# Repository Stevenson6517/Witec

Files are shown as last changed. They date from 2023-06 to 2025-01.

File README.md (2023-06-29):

# :microscope: WITec

A set of tools for interacting with and processing results from a WITec
AlphaSNOM.

> This project is currently in active development. Expect frequent
> breaking changes.

## Introduction

The tools and analysis provided by this repository attempt to recreate
some of the functionality of `ScanCtrlSpectroscopyPlus.exe` and
`WitecProject.exe` that are made available to the native Windows
installation associated with a WITec AlphaSNOM.

This repository aims to replace the proprietary `.WIP` (WitecProject
file) with an open-source [HDF5][hdf5] format that better withstands
data governance needs as they relate to external validation and
reproducibility that outlives the legacy software needed to operate this
equipment.

See a brief primer on [WITec formats](docs/witec_formats.md) for help in
understanding the data formats saved by _ScanCtrlSpectroscopyPlus_. The
analysis scripts work best on `.SPE` and `.WIP` files that have been
converted to `.hdf5` files.

[hdf5]: https://github.com/HDFGroup/hdf5

## Getting started

After cloning this repository, create a `witec` virtual environment from the
[environment.yaml](environment.yaml) file provided by this repository. Issue
the following command from a terminal navigated to the root of this project.

```python
conda env create -f environment.yaml
```

> Expect this process to take several minutes

Activate the environment before running any scripts:

```python
conda activate witec
```

See the [How To Guide](docs/how_to.md) for instructions on how to use
the instruments connected to the WITec AlphaSNOM in Stevenson 6517.

### Viewing Jupyter notebooks

Jupyter notebooks are a useful way to explore data and develop code
interactively, but they don't track well under version control. The
[jupytext][jupytext] extension for Jupyter Lab allows markdown files
(`.md`) and plain python files (`.py`) to be treated as interactive
python notebooks (`.ipynb`) while maintaining their simpler file formats
for better version control.

This project contains several Jupyter notebooks to help users understand
the scripts and types of data generated by the WITec AlphaSNOM. When you
first clone this repository, all notebooks will be in `.py` format, but
you can pair them to an interactive notebook or open them as an
interactive notebook with Jupytext. See their documentation on [paired
notebooks][jupytext-paired-notebooks] for help.

[jupytext]: https://jupytext.readthedocs.io/en/latest/
[jupytext-paired-notebooks]: https://jupytext.readthedocs.io/en/latest/paired-notebooks.html

## Contributing

Notice any errors? Tell us about them.

This lab is run by scientists, not software developers. Newcomers are welcome.
Check out our [guidelines](CONTRIBUTING.md) on how you can help.

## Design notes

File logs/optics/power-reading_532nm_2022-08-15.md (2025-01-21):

---
date: 2022-08-15
description: 'Laser power readings throughout the beampath'
measured by:
- David Curie
laser:
    - model: 'Verdi-5W'
    - serial: 'V5-G5403'
    - manufacture date: 'Dec-2004'
wavelength: 532
measurement:
    - device: 'Thorlabs PM101'
    - model: 'M00702598'
    - serial: '210608107'
    - calibration date: '2021-05-19'
    - mode: 'Mean over 4000 samples'
---

The measurements from Aug 14 suggest there is more loss than expected at each
of the microscope objectives. This suggests a misalignment of the fiber into
the microscope.

I adjusted the set screw on the SMA connector that brings the fiber into the
back of the WITec microscope until the laser spot size was minimized on the
camera. I then remeasured the power after each microscope objective.

| Location                        | Measured Power (mW) |
|---------------------------------|---------------------|
| After fiber exit                | 6.1  ± 0.3          |
| After 50x microscope objective  | 2.46 ± 0.12         |
| After 100x microscope objective | 0.84 ± 0.06         |

# Notes

- The laser from the fiber is directed down to the sample by use of a 50:50
  cube beam splitter. The theoretical maximum power that should reach the
  sample is 3 mW.
- The 100x objective has less throughput because it has a different numerical aperture (NA) than the 50x objective.
    - I have not quantified the beam size after the fiber or the theoretical throughput based on the NA. So long as I can quantify the power through the objective, I am not yet worried about optimizing the NA.

I next want to quantify the power at the sample based on various laser powers
as set by the power supply and by use of neutral density (ND) filters placed
before the objective coupling to the input of the fiber.

| Set Power (W) | ND Filter | Microscope Objective | Measured Power (µW) |
|---------------|-----------|----------------------|---------------------|
| 0.01          | ND10A     | 50x                  | 2.5  ± 0.1          |
| 0.10          | ND10A     | 50x                  | 42   ± 3            |
| 0.20          | ND10A     | 50x                  | 175  ± 8            |
| 0.30          | ND10A     | 50x                  | 380  ± 20           |
| 0.40          | ND10A     | 50x                  | 750  ± 30           |
| 0.50          | ND10A     | 50x                  | 1100 ± 50           |
| 0.60          | ND10A     | 50x                  | 1470 ± 70           |
| 0.70          | ND10A     | 50x                  | 1630 ± 70           |
| 0.80          | ND10A     | 50x                  | 1560 ± 60           |
| 0.90          | ND10A     | 50x                  | 1310 ± 60           |
| 1.00          | ND10A     | 50x                  | 960  ± 40           |
| 0.01          | ND20A     | 50x                  | 0.08 ± 0.01         |
| 0.10          | ND20A     | 50x                  | 2.0  ± 0.1          |
| 0.20          | ND20A     | 50x                  | 7.4  ± 0.4          |
| 0.30          | ND20A     | 50x                  | 18   ± 1            |
| 0.40          | ND20A     | 50x                  | 38   ± 2            |
| 0.50          | ND20A     | 50x                  | 65   ± 3            |
| 0.60          | ND20A     | 50x                  | 108  ± 5            |
| 0.70          | ND20A     | 50x                  | 155  ± 5            |
| 0.80          | ND20A     | 50x                  | 190  ± 10           |
| 0.90          | ND20A     | 50x                  | 230  ± 10           |
| 1.00          | ND20A     | 50x                  | 240  ± 10           |
| 0.01          | ND10A     | 100x                 | 0.17 ± 0.2          |
| 0.10          | ND10A     | 100x                 | 4.2  ± 0.3          |
| 0.20          | ND10A     | 100x                 | 16   ± 2            |
| 0.30          | ND10A     | 100x                 | 37   ± 2            |
| 0.40          | ND10A     | 100x                 | 69   ± 3            |
| 0.50          | ND10A     | 100x                 | 107  ± 5            |
| 0.60          | ND10A     | 100x                 | 153  ± 6            |
| 0.70          | ND10A     | 100x                 | 187  ± 7            |
| 0.80          | ND10A     | 100x                 | 215  ± 10           |
| 0.90          | ND10A     | 100x                 | 230  ± 10           |
| 1.00          | ND10A     | 100x                 | 210  ± 10           |
| 0.01          | ND20A     | 100x                 | 0.03 ± 0.01         |
| 0.10          | ND20A     | 100x                 | 0.68 ± 0.04         |
| 0.20          | ND20A     | 100x                 | 2.6  ± 0.2          |
| 0.30          | ND20A     | 100x                 | 6.4  ± 0.3          |
| 0.40          | ND20A     | 100x                 | 13.1 ± 0.6          |
| 0.50          | ND20A     | 100x                 | 23   ± 1            |
| 0.60          | ND20A     | 100x                 | 37   ± 2            |
| 0.70          | ND20A     | 100x                 | 52   ± 2            |
| 0.80          | ND20A     | 100x                 | 68   ± 4            |
| 0.90          | ND20A     | 100x                 | 80   ± 4            |
| 1.00          | ND20A     | 100x                 | 80   ± 4            |

```python
import pathlib

import matplotlib.pyplot as plt
import pandas as pd
import scienceplots

from markdown_tools import extract_data

# Gather variables from filename
filename = "power-reading_532nm_2022-08-15.md"
source = pathlib.Path(filename)
target = pathlib.Path("media") / source.name

verdi_power = extract_data(source, index=1)
# set boolean masks
ND10A = verdi_power["ND Filter"].isin(["ND10A"])
ND20A = verdi_power["ND Filter"].isin(["ND20A"])
obj_50 = verdi_power["Microscope Objective"].isin(["50x"])
obj_100 = verdi_power["Microscope Objective"].isin(["100x"])
# Use boolean masks to pick subsets of entire dataframe
ND10A_50 = verdi_power.loc[ND10A & obj_50]
ND10A_100 = verdi_power.loc[ND10A & obj_100]
ND20A_50 = verdi_power.loc[ND20A & obj_50]
ND20A_100 = verdi_power.loc[ND20A & obj_100]
# Plot each subset
with plt.style.context(["default", "science", "notebook"]):
    fig, [ax1, ax2] = plt.subplots(2, 1, figsize=(6, 8))
    fig.suptitle(source.stem)
    ND10A_50.plot(
        ax=ax1,
        y="Measured Power (µW)",
        yerr="± Measured Power (µW)",
        label="ND10A @ 50x",
    )
    ND20A_50.plot(
        ax=ax1,
        y="Measured Power (µW)",
        yerr="± Measured Power (µW)",
        label="ND20A @ 50x",
    )
    ND10A_100.plot(
        ax=ax1,
        y="Measured Power (µW)",
        yerr="± Measured Power (µW)",
        label="ND10A @ 100x",
    )
    ND20A_100.plot(
        ax=ax1,
        y="Measured Power (µW)",
        yerr="± Measured Power (µW)",
        label="ND20A @ 100x",
    )

    # Also plot weaker laser plots in separate plot for more detail
    ax2._get_lines.get_next_color()  # Skip 1st color so ax1 and ax2 match
    ND20A_50.plot(
        ax=ax2,
        y="Measured Power (µW)",
        yerr="± Measured Power (µW)",
        label="ND20A @ 50x",
    )
    ND10A_100.plot(
        ax=ax2,
        y="Measured Power (µW)",
        yerr="± Measured Power (µW)",
        label="ND10A @ 100x",
    )
    ND20A_100.plot(
        ax=ax2,
        y="Measured Power (µW)",
        yerr="± Measured Power (µW)",
        label="ND20A @ 100x",
    )
    ax1.set_ylabel("Measured Power (µW)")

    figname = target.with_suffix(".svg")
    fig.savefig(figname)
    print(f"Figure saved to {figname}")
plt.show()
```

power plots of laser at various filters and objectives Laser plots

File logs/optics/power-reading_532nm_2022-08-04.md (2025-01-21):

---
date: 2022-08-04
description: 'Laser power measurements in 6517 at the sample'
measured by:
- David Curie
- Alex Klapowitz
laser:
    - model: 'Verdi-5W'
    - serial: 'V5-G5403'
    - manufacture date: 'Dec-2004'
    - wavelength: 532
measurement:
    - device: 'Thorlabs PM101'
    - model: 'M00702598'
    - serial: '210608107'
    - calibration date: '2021-05-19'
    - mode: 'Mean over 4000 samples'
---

| Set Power (W) | ND Filter | Microscope Objective | Measured Power (µW) |
|---------------|-----------|----------------------|---------------------|
| 0.01          | None      | 50x                  | 1.62                |
| 0.02          | None      | 50x                  | 2.74                |
| 0.03          | None      | 50x                  | 3.85                |
| 0.04          | None      | 50x                  | 5.00 ± 0.14         |
| 0.05          | None      | 50x                  | 6.10 ± 0.16         |
| 0.06          | None      | 50x                  | 7.15 ± 0.2          |
| 0.07          | None      | 50x                  | 8.5  ± 0.2          |
| 0.08          | None      | 50x                  | 9.6  ± 0.2          |
| 0.09          | None      | 50x                  | 10.6 ± 0.3          |
| 0.10          | None      | 50x                  | 11.6 ± 0.3          |
| 0.11          | None      | 50x                  | 12.7 ± 0.3          |
| 0.12          | None      | 50x                  | 13.7 ± 0.3          |
| 0.13          | None      | 50x                  | 14.9 ± 0.4          |
| 0.14          | None      | 50x                  | 15.9 ± 0.5          |
| 0.15          | None      | 50x                  | 17.0 ± 0.5          |
| 0.16          | None      | 50x                  | 18.4 ± 0.4          |
| 0.17          | None      | 50x                  | 18.9 ± 0.5          |
| 0.18          | None      | 50x                  | 20.0 ± 0.5          |
| 0.19          | None      | 50x                  | 20.6 ± 0.5          |
| 0.20          | None      | 50x                  | 21.5 ± 0.6          |
| 0.25          | None      | 50x                  | 25.4 ± 0.7          |
| 0.30          | None      | 50x                  | 29.0 ± 0.7          |
| 0.35          | None      | 50x                  | 33.3 ± 0.9          |
| 0.40          | None      | 50x                  | 36.3 ± 1.0          |
| 0.45          | None      | 50x                  | 39.0 ± 1.1          |
| 0.50          | None      | 50x                  | 40.5 ± 1.1          |
| 0.55          | None      | 50x                  | 42.8 ± 0.8          |
| 0.60          | None      | 50x                  | 43.1 ± 1.1          |
| 0.01          | None      | 100x                 | 0.44 ± 0.02         |
| 0.02          | None      | 100x                 | 0.75 ± 0.02         |
| 0.03          | None      | 100x                 | 1.05 ± 0.03         |
| 0.04          | None      | 100x                 | 1.35 ± 0.04         |
| 0.05          | None      | 100x                 | 1.64 ± 0.04         |
| 0.06          | None      | 100x                 | 1.92 ± 0.05         |
| 0.07          | None      | 100x                 | 2.24 ± 0.03         |
| 0.08          | None      | 100x                 | 2.60 ± 0.06         |
| 0.09          | None      | 100x                 | 2.89 ± 0.08         |
| 0.10          | None      | 100x                 | 3.13 ± 0.08         |
| 0.11          | None      | 100x                 | 3.37 ± 0.10         |
| 0.12          | None      | 100x                 | 3.7  ± 0.1          |
| 0.13          | None      | 100x                 | 3.97 ± 0.08         |
| 0.14          | None      | 100x                 | 4.2  ± 0.1          |
| 0.15          | None      | 100x                 | 4.38 ± 0.12         |
| 0.16          | None      | 100x                 | 4.6  ± 0.1          |
| 0.17          | None      | 100x                 | 4.75 ± 0.11         |
| 0.18          | None      | 100x                 | 4.95 ± 0.15         |
| 0.19          | None      | 100x                 | 5.13 ± 0.13         |
| 0.20          | None      | 100x                 | 5.40 ± 0.14         |
| 0.25          | None      | 100x                 | 6.6  ± 0.2          |
| 0.30          | None      | 100x                 | 7.6  ± 0.2          |
| 0.35          | None      | 100x                 | 8.8  ± 0.3          |
| 0.40          | None      | 100x                 | 10.0 ± 0.3          |
| 0.45          | None      | 100x                 | 11.3 ± 0.3          |
| 0.50          | None      | 100x                 | 12.8 ± 0.4          |
| 0.55          | None      | 100x                 | 14.6 ± 0.4          |
| 0.60          | None      | 100x                 | 16.7 ± 0.4          |

```python
import pathlib

import matplotlib.pyplot as plt
import pandas as pd
import scienceplots

from markdown_tools import extract_data

# Gather variables from filename
filename = "power-reading_532nm_2022-08-04.md"
source = pathlib.Path(filename)
target = pathlib.Path("media") / source.name

verdi_power = extract_data(source)
# set boolean masks
obj_50 = verdi_power["Microscope Objective"].isin(["50x"])
obj_100 = verdi_power["Microscope Objective"].isin(["100x"])
# Use boolean masks to pick subsets of entire dataframe
verdi_50 = verdi_power.loc[obj_50]
verdi_100 = verdi_power.loc[obj_100]
# Plot each subset
with plt.style.context(["default", "science", "notebook"]):
    fig, ax = plt.subplots()
    fig.suptitle(source.stem)
    verdi_50.plot(
        ax=ax,
        y="Measured Power (µW)",
        yerr="± Measured Power (µW)",
        label="50x",
    )
    verdi_100.plot(
        ax=ax,
        y="Measured Power (µW)",
        yerr="± Measured Power (µW)",
        label="100x",
    )
    ax.set_ylabel("Measured Power (µW)")

    figname = target.with_suffix(".svg")
    fig.savefig(figname)
    print(f"Figure saved to {figname}")
plt.show()
```

power plots of laser at various objectives Laser plots

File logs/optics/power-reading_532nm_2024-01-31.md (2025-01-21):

---
date: 2024-01-31
description: 'Laser power measurements throughout the beam path'
measured by:
- David Curie
laser:
    - model: 'Verdi-5W'
    - serial: 'V5-G5403'
    - manufacture date: 'Dec-2004'
    - wavelength: 532
measurement:
    - device: 'Thorlabs PM101'
    - model: 'M00702598'
    - serial: '210608107'
    - calibration date: '2021-05-19'
    - mode: 'Mean over 5000 samples'
    - A02 responsivity: '1.0 V/W'
    - wavelength: '532 nm'
    - bandwidth: 'low'
    - attenuation: '0.00 dB'
    - beam parameters:
        - shape: 'circular'
        - diameter: '1.41 mm'
        - profile: 'flat top'
    - sensor: 'S12 QVC (200–1100 nm)'
---

I ran the LBO optimization on January 26, 2024, and am interested in the new
power profile of the output laser beam.

I cleaned both ends of the yellow single-mode fiber that runs from the Newport
fiber coupler to the back of the WITec microscope and re-aligned the 10x
microscope objective that couples the free-space laser into the fiber.

Because I realigned the free-space coupling lens, I wanted to see the power
loses at each step in the beam path to see if realignment into the fiber
affects the coupling at the back of the WITec microscope into the microscope
objectives. I was also interested to see if the beam profile of the laser is
evolving in any obvious way that would hint at at fundamental mode change with
increasing set power.

| Set power (W) | Power @ Verdi shutter (mW) | Power @ fiber out (mW) | Power @ 50x obj (mW) | Power @ 100x obj (mW) |
|---------------|----------------------------|------------------------|----------------------|-----------------------|
| 0.01          | 14.5–15.1                  | 8.8–9.3                | 2.8–3.3              | 0.8–0.9               |
| 0.02          | 24.6–25.1                  | 13.97–15.81            | 4.7–5.4              | 1.3–1.5               |
| 0.03          | 34.5–35.6                  | 19.8–22                | 6.2–7.9              | 1.8–2.1               |
| 0.04          | N/A                        | 25.6–28.6              | 8.6–9.8              | 2.36–2.74             |

I did not go above 40 mW of raw output power into the fiber to avoid burning
the fiber. Thorlabs says that the fibers are rated up to 70 mW before they meet
a permanent damage threshold.

I next want to quantify the power at the sample based on various laser powers
as set by the power supply and by use of neutral density (ND) filters placed
before the objective coupling to the input of the fiber.

| Set Power (W) | ND Filter | Microscope Objective | Min Power (µW) | Max Power (µW) |
|---------------|-----------|----------------------|----------------|----------------|
| 0.01          | ND01A     | 50x                  | 4.3            | 6.2            |
| 0.02          | ND01A     | 50x                  | 9.0            | 11.7           |
| 0.03          | ND01A     | 50x                  | 13.1           | 21.2           |
| 0.04          | ND01A     | 50x                  | 19.5           | 27.1           |
| 0.05          | ND01A     | 50x                  | 28             | 38             |
| 0.06          | ND01A     | 50x                  | 37             | 50             |
| 0.07          | ND01A     | 50x                  | 48             | 63             |
| 0.08          | ND01A     | 50x                  | 54             | 74             |
| 0.09          | ND01A     | 50x                  | 75             | 84             |
| 0.10          | ND01A     | 50x                  | 87             | 102            |
| 0.15          | ND01A     | 50x                  | 160            | 190            |
| 0.20          | ND01A     | 50x                  | 250            | 300            |
| 0.25          | ND01A     | 50x                  | 370            | 470            |
| 0.01          | ND01A     | 100x                 | 4.0            | 5.0            |
| 0.02          | ND01A     | 100x                 | 8.1            | 10.6           |
| 0.03          | ND01A     | 100x                 | 12.1           | 16.2           |
| 0.04          | ND01A     | 100x                 | 16             | 21             |
| 0.05          | ND01A     | 100x                 | 22             | 27             |
| 0.06          | ND01A     | 100x                 | 27             | 37             |
| 0.07          | ND01A     | 100x                 | 34             | 41             |
| 0.08          | ND01A     | 100x                 | 41             | 52             |
| 0.09          | ND01A     | 100x                 | 49             | 64             |
| 0.10          | ND01A     | 100x                 | 54             | 70             |
| 0.15          | ND01A     | 100x                 | 95             | 110            |
| 0.20          | ND01A     | 100x                 | 139            | 168            |
| 0.25          | ND01A     | 100x                 | 180            | 215            |
| 0.01          | ND10A     | 50x                  | 1.0            | 1.7            |
| 0.10          | ND10A     | 50x                  | 16             | 22             |
| 0.20          | ND10A     | 50x                  | 70             | 87             |
| 0.30          | ND10A     | 50x                  | 170            | 230            |
| 0.40          | ND10A     | 50x                  | 350            | 440            |
| 0.50          | ND10A     | 50x                  | 600            | 700            |
| 0.60          | ND10A     | 50x                  | 920            | 1070           |
| 0.70          | ND10A     | 50x                  | 1140           | 1300           |
| 0.80          | ND10A     | 50x                  | 1300           | 1500           |
| 0.90          | ND10A     | 50x                  | 1340           | 1400           |
| 0.01          | ND10A     | 100x                 | 0.9            | 1.4            |
| 0.02          | ND10A     | 100x                 | 1.8            | 2.6            |
| 0.03          | ND10A     | 100x                 | 3.2            | 4.1            |
| 0.04          | ND10A     | 100x                 | 3.4            | 4.8            |
| 0.05          | ND10A     | 100x                 | 5.2            | 6.6            |
| 0.06          | ND10A     | 100x                 | 7.7            | 9.0            |
| 0.07          | ND10A     | 100x                 | 8.8            | 10.7           |
| 0.08          | ND10A     | 100x                 | 10.7           | 13.9           |
| 0.09          | ND10A     | 100x                 | 13.6           | 17.2           |
| 0.10          | ND10A     | 100x                 | 15.7           | 19.1           |
| 0.15          | ND10A     | 100x                 | 30.4           | 36.3           |
| 0.20          | ND10A     | 100x                 | 48             | 58             |
| 0.25          | ND10A     | 100x                 | 65             | 76             |
| 0.30          | ND10A     | 100x                 | 90             | 111            |
| 0.35          | ND10A     | 100x                 | 113            | 140            |
| 0.40          | ND10A     | 100x                 | 141            | 167            |
| 0.45          | ND10A     | 100x                 | 209            | 241            |
| 0.50          | ND10A     | 100x                 | 240            | 270            |
| 0.55          | ND10A     | 100x                 | 255            | 293            |
| 0.60          | ND10A     | 100x                 | 320            | 340            |
| 0.65          | ND10A     | 100x                 | 330            | 370            |
| 0.70          | ND10A     | 100x                 | 360            | 410            |
| 0.75          | ND10A     | 100x                 | 390            | 450            |
| 0.80          | ND10A     | 100x                 | 410            | 465            |
| 0.85          | ND10A     | 100x                 | 360            | 410            |
| 0.90          | ND10A     | 100x                 | 390            | 440            |
| 0.01          | ND20A     | 50x                  | 0.03           | 0.04           |

```python
import pathlib

import matplotlib.pyplot as plt
from matplotlib.ticker import MultipleLocator
import pandas as pd
import scienceplots

from markdown_tools import extract_data

# Gather variables from filename
filename = "power-reading_532nm_2024-01-31.md"
source = pathlib.Path(filename)
target = pathlib.Path("media") / source.name

verdi_power = extract_data(source, index=1)
# set boolean masks
ND01A = verdi_power["ND Filter"].isin(["ND01A"])
ND10A = verdi_power["ND Filter"].isin(["ND10A"])
ND20A = verdi_power["ND Filter"].isin(["ND20A"])
obj_50 = verdi_power["Microscope Objective"].isin(["50x"])
obj_100 = verdi_power["Microscope Objective"].isin(["100x"])
# Use boolean masks to pick subsets of entire dataframe
ND01A_50 = verdi_power.loc[ND01A & obj_50]
ND01A_100 = verdi_power.loc[ND01A & obj_100]
ND10A_50 = verdi_power.loc[ND10A & obj_50]
ND10A_100 = verdi_power.loc[ND10A & obj_100]

# Plot each subset
with plt.style.context(["default", "science", "notebook"]):
    fig, ax = plt.subplots(figsize=(6, 8))
    fig.suptitle(source.stem)
    # Reserve the first two fill colors
    # for unfiltered measurements
    ax._get_patches_for_fill.get_next_color()
    ax._get_patches_for_fill.get_next_color()
    ax.fill_between(
        ND01A_50.index,
        ND01A_50["Min Power (µW)"],
        ND01A_50["Max Power (µW)"],
        label="ND01A @ 50x",
    )
    ax.fill_between(
        ND01A_100.index,
        ND01A_100["Min Power (µW)"],
        ND01A_100["Max Power (µW)"],
        label="ND01A @ 100x",
    )
    ax.fill_between(
        ND10A_50.index,
        ND10A_50["Min Power (µW)"],
        ND10A_50["Max Power (µW)"],
        label="ND10A @ 50x",
    )
    ax.fill_between(
        ND10A_100.index,
        ND10A_100["Min Power (µW)"],
        ND10A_100["Max Power (µW)"],
        label="ND10A @ 100x",
    )
    ax.legend()
    ax.xaxis.set_major_locator(MultipleLocator(0.1))
    ax.grid(True, which="both")
    ax.set_ylabel("Measured Power (µW)")
    ax.set_xlabel("Set Power (W)")
    
    plt.tight_layout()
    figname = target.with_suffix(".svg")
    fig.savefig(figname)
    print(f"Figure saved to {figname}")
plt.show()
```

power plots of laser at various filters and objectives Laser plots

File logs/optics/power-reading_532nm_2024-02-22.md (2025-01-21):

---
date: 2024-02-22
description: 'Laser power measurements throughout the beam path'
measured by:
- David Curie
laser:
    - model: 'Verdi-5W'
    - serial: 'V5-G5403'
    - manufacture date: 'Dec-2004'
    - wavelength: 532
measurement:
    - device: 'Thorlabs PM101'
    - model: 'M00702598'
    - serial: '210608107'
    - calibration date: '2021-05-19'
    - mode: 'Mean over 4000 samples'
    - A02 responsivity: '1.0 V/W'
    - wavelength: '532 nm'
    - bandwidth: 'low'
    - attenuation: '0.00 dB'
    - beam parameters:
        - shape: 'circular'
        - diameter: '1.41 mm'
        - profile: 'flat top'
    - sensor: 'S12 QVC (200–1100 nm)'
---

There is a significant amount of signal coming into the spectrometer that
doesn't appear to be any Raman signal or photoluminescence from the sample. We
know this because the signal in the spectrometer remains even after switching
samples under the microscope.

I suspected this was coming from fluorescence in the fiber, so earlier this
month I further investigated switching out the single-mode fiber in case the
fiber had a microfracture or other small defect causing scattering into the
cladding that was weakly fluorescing.

The results of my troubleshooting were detailed starting on January 25 and
continued until February 16. These notes can be found
[here](../laser/laser_alignment.md).

After this investigation, I settled on a laser alignment with a laser line
clean up filter after the fiber and before the beam splitter. My alignment is
detailed by my new power output characterizations at various points along the
beam path.

Configuration
: Verdi -> 10x objective -> SM fiber -> LL filter -> 50:50 BS -> Obj -> Sample -> Obj -> 50:50 BS -> MM out

Diode current
: 23.52 A

| Set power (W) | Location                             | Measured Power (mW) |
|---------------|--------------------------------------|---------------------|
| 0.01          | Verdi shutter                        | 14.65 ± 0.12        |
| 0.01          | Single-mode fiber out                | 8.4   ± 0.2         |
| 0.01          | Sample (50x objective)               | 2.00  ± 0.05        |
| 0.01          | Multi-mode fiber out (50x)           | 0.17  ± 0.01        |
| 0.01          | 532 LP + Multi-mode fiber out (50x)  | 0.03  ± 0.01        |
| 0.01          | Sample (100x objective)              | 0.79  ± 0.02        |
| 0.01          | Multi-mode fiber out (100x)          | 0.04  ± 0.005       |
| 0.01          | 532 LP + Multi-mode fiber out (100x) | 0.03  ± 0.01        |

I next investigated the measured power output at the sample under various
configurations. For measurements that involved a neutral density filter before
the single-mode fiber, the filter was rotated until I achieved maximum throughput.

| Set Power (W) | ND Filter | Microscope Objective | Min Power (µW) | Max Power (µW) |
|---------------|-----------|----------------------|----------------|----------------|
| 0.01          | None      | 50x                  | 1900           | 2100           |
| 0.02          | None      | 50x                  | 3250           | 3500           |
| 0.03          | None      | 50x                  | 4470           | 4970           |
| 0.04          | None      | 50x                  | 5930           | 6390           |
| 0.01          | ND01A     | 50x                  | 7.0            | 7.7            |
| 0.05          | ND01A     | 50x                  | 41             | 44             |
| 0.10          | ND01A     | 50x                  | 107            | 115            |
| 0.15          | ND01A     | 50x                  | 188            | 205            |
| 0.20          | ND01A     | 50x                  | 295            | 325            |
| 0.25          | ND01A     | 50x                  | 435            | 465            |
| 0.30          | ND01A     | 50x                  | 585            | 630            |
| 0.35          | ND01A     | 50x                  | 775            | 825            |
| 0.40          | ND01A     | 50x                  | 960            | 1020           |
| 0.45          | ND01A     | 50x                  | 1170           | 1235           |
| 0.50          | ND01A     | 50x                  | 1400           | 1500           |
| 0.01          | None      | 100x                 | 750            | 820            |
| 0.02          | None      | 100x                 | 1270           | 1370           |
| 0.03          | None      | 100x                 | 1700           | 2040           |
| 0.01          | ND01A     | 100x                 | 2.3            | 2.5            |
| 0.10          | ND01A     | 100x                 | 53             | 57             |
| 0.15          | ND01A     | 100x                 | 92             | 99             |
| 0.20          | ND01A     | 100x                 | 142            | 153            |
| 0.25          | ND01A     | 100x                 | 200            | 215            |
| 0.30          | ND01A     | 100x                 | 270            | 290            |
| 0.35          | ND01A     | 100x                 | 350            | 370            |
| 0.40          | ND01A     | 100x                 | 435            | 465            |
| 0.45          | ND01A     | 100x                 | 515            | 555            |
| 0.50          | ND01A     | 100x                 | 584            | 615            |
| 0.55          | ND01A     | 100x                 | 620            | 660            |

```python
import pathlib

import matplotlib.pyplot as plt
from matplotlib.ticker import MultipleLocator
import pandas as pd
import scienceplots

from markdown_tools import extract_data

# Gather variables from filename
filename = "power-reading_532nm_2024-02-22.md"
source = pathlib.Path(filename)
target = pathlib.Path("media") / source.name

verdi_power = extract_data(source, index=1)
# set boolean masks
ND01A = verdi_power["ND Filter"].isin(["ND01A"])
No_filter = verdi_power["ND Filter"].isin(["None"])
obj_50 = verdi_power["Microscope Objective"].isin(["50x"])
obj_100 = verdi_power["Microscope Objective"].isin(["100x"])
# Use boolean masks to pick subsets of entire dataframe
None_50 = verdi_power.loc[No_filter & obj_50]
None_100 = verdi_power.loc[No_filter & obj_100]
ND01A_50 = verdi_power.loc[ND01A & obj_50]
ND01A_100 = verdi_power.loc[ND01A & obj_100]

# Plot each subset
with plt.style.context(["default", "science"]):
    fig, [ax1, ax2] = plt.subplots(1, 2, width_ratios=[1,3], figsize=(7, 4))
    fig.suptitle(source.stem)
    
    ax1.set_title("Unfiltered power")
    ax1.xaxis.set_major_locator(MultipleLocator(0.05))
    ax1.yaxis.set_major_locator(MultipleLocator(500))
    ax1.grid(which="major")
    ax1.grid(which="minor", alpha=0.4)
    ax1.set_xlim(None, 0.05)
    ax1.set_ylabel("Measured Power (µW)")
    ax1.set_xlabel("Set Power (W)")
    ax1.fill_between(
        None_50.index,
        None_50["Min Power (µW)"],
        None_50["Max Power (µW)"],
        label="50x",
        alpha=0.5,
    )
    ax1.fill_between(
        None_100.index,
        None_100["Min Power (µW)"],
        None_100["Max Power (µW)"],
        label="100x",
        alpha=0.5,
    )
    ax1.legend(loc="upper left")

    # Skip first two fill colors
    # so that next axis picks up where previous axis left off
    ax2._get_patches_for_fill.get_next_color()
    ax2._get_patches_for_fill.get_next_color()

    ax2.set_title("Filtered power")
    ax2.xaxis.set_major_locator(MultipleLocator(0.05))
    ax2.grid(which="major")
    ax2.grid(which="minor", alpha=0.4)
    ax2.set_ylabel("Measured Power (µW)")
    ax2.set_xlabel("Set Power (W)")
    ax2.fill_between(
        ND01A_50.index,
        ND01A_50["Min Power (µW)"],
        ND01A_50["Max Power (µW)"],
        label="ND01A @ 50x",
        alpha=0.5,
    )
    ax2.fill_between(
        ND01A_100.index,
        ND01A_100["Min Power (µW)"],
        ND01A_100["Max Power (µW)"],
        label="ND01A @ 100x",
        alpha=0.5,
    )
    ax2.legend()
    
    plt.tight_layout()
    figname = target.with_suffix(".svg")
    fig.savefig(figname)
    print(f"Figure saved to {figname}")
plt.show()
```

power plots of laser at various filters and objectives Laser plots

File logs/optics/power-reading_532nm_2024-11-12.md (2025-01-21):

---
date: 2024-11-12
description: 'Laser power stability measurements'
measured by:
- Richarda Niemann
laser:
    - model: 'Verdi-5W'
    - serial: 'V5-G5403'
    - manufacture date: 'Dec-2004'
    - wavelength: 532
measurement:
    - device: 'Thorlabs PM101'
    - model: 'M00702598'
    - serial: '210608107'
    - calibration date: '2021-05-19'
    - mode: 'Mean over 4000 samples'
---

We are interested in the long-term stability of the Verdi output. We monitored
the laser power over the course of several hours. The laser has been on standby
since the night before, and we began collecting power readings shortly after
turning the laser on and maintained at its lowest setting of 0.01 W.

The power was monitored at the sample without an objective, so as to include
a standard reference for effective alignment. More exactly, the power meter was
positioned up into the vacant recessed turret that holds microscope objectives
in the WITec so that the laser readings are light-tight from inside the
microscope and would be unaffected by changes in room lighting throughout the
day.

Configuration
: Verdi -> 10x objective -> SM fiber -> LL filter -> 50:50 BS -> Obj -> Sample

Diode current
: 23.52 A

- `data/laser/Verdi-V5_plog_0010mW_f-0_23.52A_power_2024-11-12.csv`

```python
import datetime
import pathlib

import numpy as np
import matplotlib.pyplot as plt
from matplotlib.ticker import MultipleLocator
from matplotlib.dates import HourLocator, DateFormatter
import pandas as pd
import scienceplots

# Gather variables from filename
data_path = "../../data/laser/Verdi-V5_plog_0010mW_f-0_23.52A_power_2024-11-12.csv"
filename = "power-reading_532nm_2024-11-12.md"
source = pathlib.Path(filename)
target = pathlib.Path("media") / source.name

start = datetime.time(8, 15, 50)
stop_low = datetime.time(8, 18, 56)
start_high = datetime.time(8, 18, 57)
stable_cutoff = datetime.time(11, 0, 0)
stop = datetime.time(16, 20, 0)

verdi_power = pd.read_csv(data_path, skiprows=14)
verdi_power["Time (hh:mm:ss)"] = pd.to_datetime(verdi_power["Time of day (hh:mm:ss) "], format="%H:%M:%S.%f", exact=False).dt.time
stable_region = verdi_power[verdi_power["Time (hh:mm:ss)"] > stable_cutoff]["Power (W)"]
laser_mean = stable_region.mean()
laser_std = stable_region.std()
laser_variance = laser_std ** 2

with plt.style.context(["default", "science", "notebook"]):
    fig, [ax1, ax2] = plt.subplots(1, 2, width_ratios=(1,15), figsize=(10,7))
    fig.suptitle(source.stem)
    verdi_power.plot(ax=ax1, x="Time (hh:mm:ss)", y="Power (W)", xlim=(start, stop_low), ylim=(0, 7e-4))
    ax1.set_ylabel("Measured Power (W)")
    ax1.set_xlabel("")
    ax1.xaxis.set_ticks(ticks=(start,))
    
    verdi_power.plot(ax=ax2, x="Time (hh:mm:ss)", y="Power (W)", xlim=(start_high, stop), ylim=(2.4e-3, None), lw=0.1)
    ax2.hlines(y=laser_mean - laser_std, xmin=stable_cutoff, xmax=stop, colors="C3")
    ax2.hlines(y=laser_mean, xmin=stable_cutoff, xmax=stop, colors="C1")
    ax2.hlines(y=laser_mean + laser_std, xmin=stable_cutoff, xmax=stop, colors="C3")
    ax2.annotate(f"Stability (2σ/µ): {2 * laser_std/laser_mean:.3f}",
                 xy=(0.5, 0.75), xycoords='figure fraction')
    ax2.annotate(f"Summary: {stable_region.describe().to_string()}",
                 xy=(0.5, 0.20), xycoords='figure fraction')
    ax2.yaxis.tick_right()
    
    for ax in [ax1, ax2]:
        ax.grid(which="minor", alpha=0.4)
        ax.grid(which="major")
        ax.get_legend().remove()
        ax.ticklabel_format(axis="y", style="sci", scilimits=(-2,2))

    fig.autofmt_xdate()
    fig.subplots_adjust(wspace=0, hspace=0)
    figname = target.with_suffix(".svg")
    fig.savefig(figname)
    print(f"Figure saved to {figname}")
plt.show()
```

Power stability from startup Power stability

> At 8:18, we realized the additional 50:50 beam splitter prism that directs
white light onto the sample was still in place. It was removed from the path
and the remaining measurements for the day are logged as intended.

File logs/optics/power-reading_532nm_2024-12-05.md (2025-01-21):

---
date: 2024-12-05
description: 'Laser power tunability measurements'
measured by:
- David Curie
laser:
    - model: 'Verdi-5W'
    - serial: 'V5-G5403'
    - manufacture date: 'Dec-2004'
    - wavelength: 532
measurement:
    - device: 'Thorlabs PM101'
    - model: 'M00702598'
    - serial: '210608107'
    - calibration date: '2021-05-19'
    - mode: 'Mean over 4000 samples'
---

I placed the ND filter immediately before the 10x focusing objective that
couples the free-space Verdi laser output into the single-mode fiber.
I situated the power meter roughly at focus of the 50x objective, being
careful not to come to a tight focus. This is so that I do not damage the
sensor at high laser power where the power per unit area can be exceptionally
large, even though the overall power is within the detectable power range of
the sensor (0–30 mW). I jointly monitored the camera feed of the reflected
laser light as if I were viewing a sample.

I notice that the apparent beam profile changes when I place any number of ND
filters in the beam path. This is evident by larger scattering artifacts in
the camera feed, such as a starburst pattern of the reflected light from the
internal beam splitters and a less-pronounced focused beam spot size when
viewing a sample in the microscope.

I rotated the ND filter around its central axis like hands on a clock until
I achieved the smallest measured power after the objective. This resulted in
the least intense starburst artifacts. I then adjusted the requested laser
power on the front panel controls and recorded the measured power at the sample
for various settings.

Configuration
: Verdi -> ND filter -> 10x objective -> SM fiber -> LL filter -> 50:50 BS -> Obj -> Sample

| Set Power (W) | ND Filter | Microscope Objective | Min Power (µW) | Max Power (µW) | Mean Power (µW) | Diode Current (A) |
|---------------|-----------|----------------------|----------------|----------------|-----------------|-------------------|
| 0.01          | None      | 50x                  | 1900           | 2100           | 2100 ± 100      | 23.54             |
| 0.02          | None      | 50x                  | 3300           | 3800           | 3500 ± 200      | 24.00             |
| 0.03          | None      | 50x                  | 4400           | 5600           | 4900 ± 200      | 24.29             |
| 0.01          | ND01A     | 50x                  | 0.43           | 0.50           | 0.45 ± 0.02     | 23.54             |
| 0.05          | ND01A     | 50x                  | 1.95           | 2.34           | 2.1  ± 0.1      | 24.71             |
| 0.10          | ND01A     | 50x                  | 4.7            | 5.6            | 5.3  ± 0.2      | 25.29             |
| 0.15          | ND01A     | 50x                  | 10.1           | 12.0           | 11.5 ± 0.4      | 25.59             |
| 0.20          | ND01A     | 50x                  | 19.7           | 23.5           | 22.4 ± 0.9      | 25.81             |
| 0.25          | ND01A     | 50x                  | 35.7           | 41.7           | 40.0 ± 1.5      | 25.99             |
| 0.30          | ND01A     | 50x                  | 62.5           | 73.9           | 70.7 ± 3.0      | 26.09             |
| 0.35          | ND01A     | 50x                  | 101.8          | 121.3          | 115  ± 5        | 26.26             |
| 0.40          | ND01A     | 50x                  | 162            | 192            | 182  ± 7        | 26.33             |
| 0.45          | ND01A     | 50x                  | 280            | 330            |                 | 26.38             |
| 0.45          | ND01A     | 50x                  | 450            | 490            |                 | 26.38             |
| 0.01          | ND01A     | 50x                  | 3.05           | 3.50           | 3.13 ± 0.13     | 23.55             |

When I reached a set power of 0.45 W, I noticed a runaway increase in measured
power at the sample. During this time, the diode current remained steady, and
there were no alerts on the front panel indicating "LASER SEEKING". This
gradual increase in power happened over several minutes. After I set the power
to 450 mW at 17:12, the measured power immediately read around (280–330 µW),
but by 17:16, this reading was (450–490 µW).

I began to suspect that the surface of the reflective ND filter was absorbing
a small amount of the laser power and that the ND coating was breaking down,
so I reduced the laser power and measured a baseline reading at a set power of
0.01 W. This showed a much higher measured power than I initially controlled
for when I rotated the filter to its minimum reading.

There is a chance that this discrepancy in power readings is a result of
hysteresis in the laser diode, so I will return back tomorrow to see if
a fresh start from standby will eliminate this bias.

```python
import pathlib

import matplotlib.pyplot as plt
from matplotlib.ticker import MultipleLocator
import pandas as pd
import scienceplots

from markdown_tools import extract_data

# Gather variables from filename
filename = "power-reading_532nm_2024-12-05.md"
source = pathlib.Path(filename)
target = pathlib.Path("media") / source.name

verdi_power = extract_data(source, index=0)
# set boolean masks
ND01A = verdi_power["ND Filter"].isin(["ND01A"])
No_filter = verdi_power["ND Filter"].isin(["None"])
obj_50 = verdi_power["Microscope Objective"].isin(["50x"])
obj_100 = verdi_power["Microscope Objective"].isin(["100x"])
# Use boolean masks to pick subsets of entire dataframe
None_50 = verdi_power.loc[No_filter & obj_50]
None_100 = verdi_power.loc[No_filter & obj_100]
ND01A_50 = verdi_power.loc[ND01A & obj_50]
ND01A_100 = verdi_power.loc[ND01A & obj_100]

# Plot each subset
with plt.style.context(["default", "science"]):
    fig, [ax1, ax2] = plt.subplots(1, 2, width_ratios=[1,7], figsize=(7, 4))
    fig.suptitle(source.stem)
    
    ax1.set_title("Unfiltered\npower")
    ax1.yaxis.set_major_locator(MultipleLocator(500))
    ax1.set_xlim(None, 0.035)
    ax1.fill_between(
        None_50.index,
        None_50["Min Power (µW)"],
        None_50["Max Power (µW)"],
        label="50x",
        alpha=0.5,
    )
    ax1.errorbar(
        x=None_50.index,
        y=None_50["Mean Power (µW)"],
        yerr=None_50["± Mean Power (µW)"],
    )
    ax1.legend(loc="upper left")
    
    # Skip first two fill colors and line colors
    # so that next axis picks up where previous axis left off
    ax2._get_patches_for_fill.get_next_color()
    ax2._get_patches_for_fill.get_next_color()
    ax2._get_lines.get_next_color()
    ax2._get_lines.get_next_color()
    ax2.fill_between(
        ND01A_50.index,
        ND01A_50["Min Power (µW)"],
        ND01A_50["Max Power (µW)"],
        label="ND01A @ 50x",
        alpha=0.5,
    )
    ax2.errorbar(
        x=ND01A_50.index,
        y=ND01A_50["Mean Power (µW)"],
        yerr=ND01A_50["± Mean Power (µW)"],
    )
    ax2.set_title("Filtered power")
    ax2.yaxis.set_label_position("right")
    ax2.yaxis.tick_right()
    ax2.legend()

    for ax in [ax1, ax2]:
        ax.xaxis.set_major_locator(MultipleLocator(0.05))
        ax.grid(which="major")
        ax.grid(which="minor", alpha=0.4)
        ax.set_xlabel("Set Power (W)")
        ax.set_ylabel("Measured Power (µW)")
    
    fig.subplots_adjust(wspace=0, hspace=0)
    figname = target.with_suffix(".svg")
    fig.savefig(figname)
    print(f"Figure saved to {figname}")
plt.show()
```

power plots of laser at various filters and objectives Laser plots

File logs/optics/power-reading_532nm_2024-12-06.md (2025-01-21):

---
date: 2024-12-06
description: 'Laser power tunability measurements'
measured by:
- David Curie
laser:
    - model: 'Verdi-5W'
    - serial: 'V5-G5403'
    - manufacture date: 'Dec-2004'
    - wavelength: 532
measurement:
    - device: 'Thorlabs PM101'
    - model: 'M00702598'
    - serial: '210608107'
    - calibration date: '2021-05-19'
    - mode: 'Mean over 4000 samples'
---

Yesterday's power readings gave me cause for inspection on the integrity of the
neutral density filters.

The theoretical transmission through ND = 0.1 is approximately 80% of the
unattenuated power. For an unfiltered measured power of 2.1 mW at the sample,
placing an ND = 0.1 filter in the beam path should reduce this effective power
at the sample to 1.7 mW, yet we are measuring anywhere from 0.5 µW to 50 µW
depending on the orientation of the ND filter.

Yesterday, I measured the power with the ND filter rotated to its minimum
throughput. My operating assumption was that because this minimized the
artifacts I saw of the reflected laser light in the video feed that this
orientation was using the least adulterated section of a worn ND filter.

Today, I tried measuring the laser power with the ND filter rotated to its
maximum throughput. My assumption here is that any burning or ablating of the
surface of the ND filter would already be done, and that I could operate at
lower power and reduce any further damage, thereby ensuring steady-state
results.

Because I noticed the steady growth in measured laser power at a setting of
0.45 W, I checked to see if this behavior happened under the new filter
orientation.

I turned the laser on from standby with a set power of 0.01 W and waited one
hour. During this time I configured the ND filter for maximum throughput as
measured at the 50x objective. The unfiltered reading was still around 2.1 mW,
and the new filtered reading was around 50 µW.

After approximately one hour, I set the laser power to 0.45 W. The initial
filtered reading at the 50x objective was around 3 mW, and within several
minutes this measurement reduced to 1.4 mW. This seems to me to indicate
continued burning of the surface of the ND filter.

When I reduced the power to 0.01 W, the measured filter laser power no longer
read 50 µW but was instead closer to 5 µW.

I rotated the filter to again be at a local maximum in terms of measured
throughput. This was again somewhere around 50 µW, but notably at a different
filter orientation than before.

I then increased the power to 0.2 W and monitored the filtered measured output
at the 50x objective to be around 1.4 mW. After about 10 minutes, this reading
remained at 1.4 mW, with no obvious signs of drift. This tells me either that
the laser output is more locally stable under a setting of 0.2 W than at
0.45 W, or that we are now operating under a regime where the ND filter is not
breaking down.

This particular model of Thorlabs ND filters (ND01A, ND02A, ND10A, etc) has
a rated damage threshold of 5 W/cm under a CW laser. The Verdi laser beam at
the shutter exit is approximately 0.5 cm. Under an assumed uniform
step-function beam profile, this means the Verdi has an average linear power
density of 0.45 W/0.5 cm or 0.9 W/cm. In practice, a Gaussian beam profile has
roughly 2x the peak intensity at the center of the beam, so the highest linear
power density under a set power of 0.45 W may be closer to 2 W/cm. This is
still below the rated damage threshold, but assumes no surface imperfections or
dust on the ND filter.

My conclusion is that we may be operating close to the breakdown limits of the
ND filter when using the Verdi at 0.45 W. I instead advocate that we rotate the
ND filter for maximum throughput, even though we may be slightly affecting the
beam profile by passing through previously affected regions of the ND filter,
so that we may operate at lower power and maintain a uniform operating
procedure based on assumed repeatable conditions.

This conclusion slightly bothers me on principle because I still expect
a filter with ND = 0.1 to transmit roughly 80% of its incident power, and
neither of these ND filter orientations gets us remotely close to that limit.
One potential solution worth investigating in the future is whether the
presence of the ND filter severely distorts, translates, or focuses the beam
profile enough to warrant a completely new re-alignment into the fiber when
a filter is present. I hesitate to explore this solution because it would
warrant a completely new alignment each time we wanted to adjust the range of
accessible powers at our sample. If we are truly operating at 80% transmission
with a filter of ND = 0.1, this also means that we should not exceed a set
laser power of 0.06 W such that the transmitted power into the fiber does not
exceed roughly 50 mW, or the approximate rated power threshold for our
single-mode fiber.

By extension of this conclusion, if we later decide that operating at a steady
laser output of 0.4 W or something significantly higher than the lowest
available powers around 0.01 W is a more appropriate consideration for the
health of the laser diode, then we are limited in our ability to exceed 0.45 W
because of our perceived belief that the ND filters begin to break down at or
above this setting.

---

I now seek to quantify the measured laser power at the sample under various
operating conditions with the new understanding that we must use the ND filter
rotated to the highest throughput so that we may benefit from appreciable power
at the sample while still maintaining relatively low operating powers.

After setting the power, I waited at least 30 seconds for the laser to finish
"LASER SEEKING". In some cases, the "LASER SEEKING" alert didn't disappear
after waiting several minutes. I then recorded the measured power statistics
anyway but made note of this behavior.

Configuration
: Verdi -> ND filter -> 10x objective -> SM fiber -> LL filter -> 50:50 BS -> Obj -> Sample

| Set Power (W) | ND Filter | Microscope Objective | Min Power (µW) | Max Power (µW) | Mean Power (µW) | Diode Current (A) | LASER SEEKING? |
|---------------|-----------|----------------------|----------------|----------------|-----------------|-------------------|----------------|
| 0.01          | None      | 50x                  | 1710           | 2360           | 2100 ± 100      | 23.52             | No             |
| 0.02          | None      | 50x                  | 3230           | 3710           | 3500 ± 150      | 23.97             | No             |
| 0.03          | None      | 50x                  | 4610           | 5320           | 5000 ± 200      | 24.25             | No             |
| 0.04          | None      | 50x                  | 6000           | 6850           | 6400 ± 300      | 24.51             | No             |
| 0.01          | ND01A     | 50x                  | 61             | 89             | 74   ± 4        | 23.51             | No             |
| 0.05          | ND01A     | 50x                  | 293            | 360            | 320  ± 15       | 24.67             | Yes            |
| 0.10          | ND01A     | 50x                  | 645            | 731            | 670  ± 30       | 25.22             | No             |
| 0.15          | ND01A     | 50x                  | 980            | 1110           | 1040 ± 40       | 25.57             | No             |
| 0.20          | ND01A     | 50x                  | 1290           | 1460           | 1370 ± 60       | 25.80             | No             |
| 0.25          | ND01A     | 50x                  | 1590           | 1790           | 1680 ± 80       | 25.93             | No             |
| 0.30          | ND01A     | 50x                  | 1830           | 2070           | 1910 ± 80       | 26.06             | No             |
| 0.25          | ND01A     | 50x                  | 1350           | 1520           | 1440 ± 60       | 25.93             | No             |
| 0.20          | ND01A     | 50x                  | 1000           | 1142           | 1060 ± 40       | 25.80             | No             |
| 0.15          | ND01A     | 50x                  | 732            | 836            | 800  ± 30       | 23.58             | No             |
| 0.10          | ND01A     | 50x                  | 480            | 560            | 520  ± 20       | 25.23             | No             |
| 0.05          | ND01A     | 50x                  | 227            | 260            | 245  ± 15       | 24.68             | Yes            |
| 0.01          | ND01A     | 50x                  | 52             | 62             | 58   ± 3        | 23.51             | No             |
| 0.01          | None      | 100x                 | 630            | 738            | 680  ± 30       | 23.51             | Yes            |
| 0.02          | None      | 100x                 | 1015           | 1320           | 1120 ± 30       | 23.97             | No             |
| 0.03          | None      | 100x                 | 1530           | 1760           | 1640 ± 60       | 24.26             | No             |
| 0.04          | None      | 100x                 | 1920           | 2400           | 2150 ± 80       | 24.51             | No             |
| 0.01          | ND01A     | 100x                 | 22             | 26             | 24 ± 1          | 23.54             | Yes            |
| 0.05          | ND01A     | 100x                 | 100            | 115            | 107 ± 5         | 24.67             | Yes            |
| 0.10          | ND01A     | 100x                 | 217            | 244            | 230 ± 10        | 25.26             | No             |
| 0.15          | ND01A     | 100x                 | 315            | 360            | 340 ± 15        | 25.58             | Yes            |
| 0.20          | ND01A     | 100x                 | 400            | 450            | 430 ± 20        | 25.80             | No             |
| 0.25          | ND01A     | 100x                 | 470            | 535            | 510 ± 20        | 25.96             | No             |
| 0.30          | ND01A     | 100x                 | 440            | 500            | 460 ± 20        | 26.07             | No             |
| 0.25          | ND01A     | 100x                 | 340            | 385            | 360 ± 20        | 25.96             | No             |
| 0.20          | ND01A     | 100x                 | 260            | 300            | 280 ± 15        | 25.80             | No             |
| 0.15          | ND01A     | 100x                 | 200            | 230            | 215 ± 10        | 25.58             | No             |
| 0.10          | ND01A     | 100x                 | 132            | 150            | 144 ± 5         | 25.28             | No             |
| 0.05          | ND01A     | 100x                 | 64             | 74             | 69 ± 3          | 24.70             | Yes            |
| 0.01          | ND01A     | 100x                 | 16             | 19             | 18 ± 2          | 23.51             | No             |

```python
import pathlib

import matplotlib.pyplot as plt
from matplotlib.ticker import MultipleLocator
import pandas as pd
import scienceplots

from markdown_tools import extract_data

# Gather variables from filename
filename = "power-reading_532nm_2024-12-06.md"
source =pathlib.Path(filename)
target = pathlib.Path("media") / source.name

verdi_power = extract_data(source, index=0)
# set boolean masks
ND01A = verdi_power["ND Filter"].isin(["ND01A"])
No_filter = verdi_power["ND Filter"].isin(["None"])
obj_50 = verdi_power["Microscope Objective"].isin(["50x"])
obj_100 = verdi_power["Microscope Objective"].isin(["100x"])
# Use boolean masks to pick subsets of entire dataframe
None_50 = verdi_power.loc[No_filter & obj_50]
None_100 = verdi_power.loc[No_filter & obj_100]
ND01A_50 = verdi_power.loc[ND01A & obj_50]
ND01A_100 = verdi_power.loc[ND01A & obj_100]

# Plot each subset
with plt.style.context(["default", "science"]):
    fig, [ax1, ax2] = plt.subplots(1, 2, width_ratios=[1,6], figsize=(7, 4))
    fig.suptitle(source.stem)
    
    ax1.set_title("Unfiltered\npower")
    ax1.yaxis.set_major_locator(MultipleLocator(500))
    ax1.set_xlim(None, 0.045)
    ax1.fill_between(
        None_50.index,
        None_50["Min Power (µW)"],
        None_50["Max Power (µW)"],
        label="50x",
        alpha=0.5,
    )
    ax1.errorbar(
        x=None_50.index,
        y=None_50["Mean Power (µW)"],
        yerr=None_50["± Mean Power (µW)"],
    )
    ax1.fill_between(
        None_100.index,
        None_100["Min Power (µW)"],
        None_100["Max Power (µW)"],
        label="100x",
        alpha=0.5,
    )
    ax1.errorbar(
        x=None_100.index,
        y=None_100["Mean Power (µW)"],
        yerr=None_100["± Mean Power (µW)"],
    )
    ax1.legend(loc="upper left")

    # Skip first fill colors and line colors
    # so that next axis picks up where previous axis left off
    ax2._get_patches_for_fill.get_next_color()
    ax2._get_lines.get_next_color()

    ax2.set_title("Filtered power")
    ax2.yaxis.set_label_position("right")
    ax2.yaxis.tick_right()
    ax2.set_ylim(0, 2100)
    ax2.fill_between(
        None_100.index,
        None_100["Min Power (µW)"],
        None_100["Max Power (µW)"],
        alpha=0.5,
    )
    ax2.errorbar(
        x=None_100.index,
        y=None_100["Mean Power (µW)"],
        yerr=None_100["± Mean Power (µW)"],
    )
    ax2.fill_between(
        ND01A_50.index,
        ND01A_50["Min Power (µW)"],
        ND01A_50["Max Power (µW)"],
        label="ND01A @ 50x",
        alpha=0.5,
    )
    ax2.errorbar(
        x=ND01A_50.index,
        y=ND01A_50["Mean Power (µW)"],
        yerr=ND01A_50["± Mean Power (µW)"],
    )
    ax2.fill_between(
        ND01A_100.index,
        ND01A_100["Min Power (µW)"],
        ND01A_100["Max Power (µW)"],
        label="ND01A @ 100x",
        alpha=0.5,
    )
    ax2.errorbar(
        x=ND01A_100.index,
        y=ND01A_100["Mean Power (µW)"],
        yerr=ND01A_100["± Mean Power (µW)"],
    )
    ax2.legend()

    for ax in [ax1, ax2]:
        ax.xaxis.set_major_locator(MultipleLocator(0.05))
        ax.grid(which="major")
        ax.grid(which="minor", alpha=0.4)
        ax.set_xlabel("Set Power (W)")
        ax.set_ylabel("Measured Power (µW)")
    
    fig.subplots_adjust(wspace=0, hspace=0)
    figname = target.with_suffix(".svg")
    fig.savefig(figname)
    print(f"Figure saved to {figname}")
plt.show()
```

power plots of laser at various filters and objectives Laser plots

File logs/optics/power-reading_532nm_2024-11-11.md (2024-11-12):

---
date: 2024-11-11
description: 'Laser power measurements throughout the beam path'
measured by:
- David Curie
- Richarda Niemann
laser:
    - model: 'Verdi-5W'
    - serial: 'V5-G5403'
    - manufacture date: 'Dec-2004'
    - wavelength: 532
measurement:
    - device: 'Thorlabs PM101'
    - model: 'M00702598'
    - serial: '210608107'
    - calibration date: '2021-05-19'
    - mode: 'Mean over 4000 samples'
---

After realizing that the laser power fluctuates at the sample because of the
observed irregularities at the single-mode fiber output and not because of poor
alignment inside the microscope, I suspected that the laser may be mode hopping
at lower power. I suspect these mode hops to occur only when moving through
certain power thresholds, or when the diode current changes as a result of
requesting higher set power.

I began to wonder if the alignment into the single-mode fiber from the Verdi
output is tuned to an inappropriate laser mode. I know that the Verdi
guarantees the I~00~ mode of a Gaussian profile. I further know that any modes
that aren't the fundamental Gaussian mode are severely attenuated in
a single-mode fiber, such that single-mode fibers can reasonably guarantee
I~00~ transmission, even if the Verdi did have weak non-fundamental Gaussian
transmission.

Because we are dealing with non-standard operating powers, I have doubts on the
reasonable guarantee of I~00~ transmission from the Verdi output and whether
2 meters of single-mode fiber is enough to filter out any modes other than
I~00~.

I wanted to observe the focused laser spot under a microscope objective to see
if the laser spot changes as a result of increased laser power. Because of the
increased laser power involved in this investigation, I insist to use
a protective neutral density filter before the 10x objective that couples the
Verdi output into the single-mode fiber. I wanted to check the laser spot in a focused video feed as a function of laser power to see if there is an obvious shift in the focused profile.

Unfortunately, the laser spot size is difficult to discern at higher set powers
in a camera feed with a filter in place, and it is unclear if the spot size is
affected by the filter or from operating at a higher set laser power (0.1 W).

I instead attempted to quantify this difference in spot size numerically.
I already know the measured power through each objective varies non-linearly as
a function of set laser power, but I have never visually quantified the focused
laser spot as a function of input coupling alignment. If the alignment into the
single-mode fiber is tuned to an inappropriate laser mode, my hope is that the
focused spot size changes size or shape with purposeful misalignment of the
Verdi laser. My assumption for this is that an improper laser mode will exit
the single-mode fiber at a slight angle other than the typical divergence cone
associated with the I~00~ transmission, and that this exit angle will
correspond approximately to the angle of the laser light coming into the fiber
(assuming a non-normal incidence to the fiber core). If we are focusing an
incorrect mode onto the sample, the location of the laser spot should be
dependent on the orientation of the laser incidence into the fiber.

I observed no such change in the focused beam spot for various misalignments.
Two explanations are likely. It is possible the output orientation of the
transmitted laser light is too slight of an adjustment with the misalignments,
and in all such misaligned cases, the laser beam—after having been collimated
inside the WITec—fills the back of the microscope objective in all cases. This
would render the spot size as a limited subset of the true beam profile, whose
propagation mode yet remains undetermined, but whose profile changes as
a function of laser diode current. The simpler conclusion is that the
transmission mode is indeed I~00~ in all cases, and that the laser profile from
the Verdi is uniformly I~00~ as stated by the manufacturer. This then implies
that the non-monotonic power response of the Verdi is related to the diode
current, which is discovered to change across certain power thresholds.

---

After previous purposeful misalignments into the single-mode fiber, I attempted
to get back to my optimum alignment, signaled by a single-mode fiber output of
9.1 mW.

I did not have as much luck or persistence, and after several hours of diligent
tweaking, called the alignment good enough. My quantified results of the system
are listed below.

Configuration
: Verdi -> 10x objective -> SM fiber -> LL filter -> 50:50 BS -> Obj -> Sample -> Obj -> 50:50 BS -> MM assembly out

Diode current
: 23.42 A

| Set power (W) | Location                    | Measured Power (mW) |
|---------------|-----------------------------|---------------------|
| 0.01          | Single-mode fiber out       | 8.3    ± 0.3        |
| 0.01          | Sample (no objective)       | 2.6    ± 0.09       |
| 0.01          | Sample (50x objective)      | 1.91   ± 0.07       |
| 0.01          | Multi-mode fiber out (50x)  | 0.17   ± 0.01       |
| 0.01          | Sample (100x objective)     | 0.64   ± 0.02       |
| 0.01          | Multi-mode fiber out (100x) | 0.078  ± 0.003      |

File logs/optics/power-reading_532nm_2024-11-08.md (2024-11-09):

---
date: 2024-11-08
description: 'Laser power measurements at increasing power'
measured by:
- David Curie
laser:
    - model: 'Verdi-5W'
    - serial: 'V5-G5403'
    - manufacture date: 'Dec-2004'
    - wavelength: 532
measurement:
    - device: 'Thorlabs PM101'
    - model: 'M00702598'
    - serial: '210608107'
    - calibration date: '2021-05-19'
    - mode: 'Mean over 4000 samples'
---

We previously observed a non-linear correspondence between the set power from
the Verdi control panel and the measured laser power at the sample through each
of the 50x or 100x objectives. I want to investigate if this non-linear
response is from a poor alignment into the fiber and/or objectives, or if this
is a response from the laser itself.

I monitored the power directly from the single-mode fiber recently aligned to
the Verdi output from November 6, 2024. To allow me to increase the laser power
beyond the damage threshold of the fiber, I attenuated the laser with
a Thorlabs neutral density filter with OD 2 (ND020A).

I began my investigation informally by quickly checking the low-power readings
at set power values of 0.01 W, 0.1 W, 0.2 W, and 0.3 W. After it was clear that
the measured power at the output of the single-mode fiber was not linearly
correlated with the set power, I began a more systematic documentation of the
results.

Configuration
: Verdi -> ND020A -> 10x objective -> SM fiber

Procedure
: Set power, wait ~10 seconds, read avg power over 4000 measurements directly at fiber tip

| Set Power (W) | Measured Power (µW) | Diode current (A) |
|---------------|---------------------|-------------------|
| 0.4           | 189                 |                   |
| 0.5           | 312                 |                   |
| 0.6           | 470                 |                   |
| 0.7           | 640                 |                   |
| 0.8           | 775                 |                   |
| 0.9           | 850                 |                   |
| 1.0           | 865                 |                   |
| 1.1           | 690                 |                   |
| 1.2           | 565                 |                   |
| 1.3           | 430                 |                   |
| 1.4           | 280                 |                   |
| 1.3           | 1130                |                   |
| 1.2           | 1150                |                   |
| 1.1           | 975                 |                   |
| 1.0           | 860                 |                   |
| 0.9           | 680                 |                   |
| 0.8           | 520                 |                   |
| 0.7           | 374                 | 26.49 A           |
| 0.6           | 252                 |                   |
| 0.5           | 157                 | 26.39 A           |
| 0.4           | 92                  | 26.28 A           |
| 0.3           | 45                  | 26.03 A           |
| 0.2           | 20                  | 25.78 A           |
| 0.1           | 5.7                 | 25.22 A           |
| 0.01          | 0.6                 | 23.46 A           |

I realized part way through my measurements that the diode current changed as
a function of the requested set power, so I began documenting this parameter as
well. I further realized that the response between the set power and measured
power was different when I ramped up the laser power versus when I ramped down
the laser power, with a more apparent linear response from the diode when the
laser ramped down from high power.

I am not yet convinced whether the non-linear correspondence between the set
power and measured power is a result of improper fiber alignment or from an
irregularity in the laser diode, although I have suspicions it is from the
latter.

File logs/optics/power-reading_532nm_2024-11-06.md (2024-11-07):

---
date: 2024-11-06
description: 'Laser power measurements throughout the beam path'
measured by:
- David Curie
laser:
    - model: 'Verdi-5W'
    - serial: 'V5-G5403'
    - manufacture date: 'Dec-2004'
    - wavelength: 532
measurement:
    - device: 'Thorlabs PM101'
    - model: 'M00702598'
    - serial: '210608107'
    - calibration date: '2021-05-19'
    - mode: 'Mean over 4000 samples'
---

I am not happy with the touch-up alignment from November 5, 2024. My cause for
alarm is the significantly reduced output at the sample under the 100x
objective. I spent more time today touching up alignment into the single-mode
fiber.

Configuration
: Verdi -> 10x objective -> SM fiber -> LL filter -> 50:50 BS -> Obj -> Sample -> Obj -> 50:50 BS -> MM assembly out

Diode current
: 23.52 A

| Set power (W) | Location                             | Measured Power (mW) |
|---------------|--------------------------------------|---------------------|
| 0.01          | Single-mode fiber out                | 9.1   ± 0.4         |

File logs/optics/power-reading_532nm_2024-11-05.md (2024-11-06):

---
date: 2024-11-05
description: 'Laser power measurements throughout the beam path'
measured by:
- David Curie
- Richarda Niemann
laser:
    - model: 'Verdi-5W'
    - serial: 'V5-G5403'
    - manufacture date: 'Dec-2004'
    - wavelength: 532
measurement:
    - device: 'Thorlabs PM101'
    - model: 'M00702598'
    - serial: '210608107'
    - calibration date: '2021-05-19'
    - mode: 'Mean over 4000 samples'
---

We modified the multi-mode fiber that comes out of the WITec microscope and
into the spectrometer to now enter a motorized assembly to couple the output
light either into a spectrometer or a Hanbury Brown–Twiss interferometer by way
of two multi-mode fibers.

During routine alignment into the multi-mode fiber assembly, we regularly
attenuate the laser power. We bumped the single-mode fiber that accepts the
Verdi free-space laser, so we thought it best to re-align the single-mode fiber
to the Verdi output.

Configuration
: Verdi -> 10x objective -> SM fiber -> LL filter -> 50:50 BS -> Obj -> Sample -> Obj -> 50:50 BS -> MM assembly out

Diode current
: 23.42 A

| Set power (W) | Location                             | Measured Power (mW) |
|---------------|--------------------------------------|---------------------|
| 0.01          | Verdi shutter                        | 14.42 ± 0.2        |
| 0.01          | Single-mode fiber out                | 8.1   ± 0.2         |
| 0.01          | Sample (50x objective)               | 1.10  ± 0.03        |
| 0.01          | Sample (100x objective)              | 0.34  ± 0.01        |

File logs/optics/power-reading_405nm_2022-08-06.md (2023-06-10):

---
date: 2022-08-06 19:38:00 CDT
description: 'Laser power measurements in 6517 at the sample'
measured by:
- David Curie
laser:
    - wavelength: 405
measurement:
    - device: 'Thorlabs PM101'
    - model: 'M00702598'
    - serial: '210608107'
    - calibration date: '2021-05-19'
    - mode: 'Mean over 4000 samples'
---

| Set Power  (W) | ND Filter | Microscope Objective | Measured Power (µW) |
|----------------|-----------|----------------------|---------------------|
| N/A            | None      | 50x                  | 36.7 ± 0.1          |
| N/A            | None      | 100x                 | 6.02 ± 0.01         |

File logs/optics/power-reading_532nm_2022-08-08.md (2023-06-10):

---
date: 2022-08-08
description: 'Laser power readings throughout the beampath'
measured by:
- David Curie
laser:
    - model: 'Verdi-5W'
    - serial: 'V5-G5403'
    - manufacture date: 'Dec-2004'
    - wavelength: 532
measurement:
    - device: 'Thorlabs PM101'
    - model: 'M00702598'
    - serial: '210608107'
    - calibration date: '2021-05-19'
    - mode: 'Mean over 4000 samples'
---

The measurements from Aug 04 suggest there is a significant loss of power
throughout the optical system. The measurements below are an attempt to isolate
where the attenuation is coming from.

| Set Power (W) | Location           | Measured Power (mW) |
|---------------|--------------------|---------------------|
| 0.01          | Verdi exit shutter | 13.45 ± 0.12        |
| 0.01          | Fiber exit         | 5.3 ± 0.3           |
| 0.02          | Verdi exit shutter | 23.1  ± 0.1         |
# Notes

- The power at the Verdi exit behaves normally; when set at a nominal 10 mW,
  the actual power is measured around 10 mW.
- Potential sources of loss:
    - Attenuation through the fiber (rated for wrong wavelength)
    - Poor coupling from free-space into the fiber (misaligned objective lens)

## Conclusions

- Need to check alignment of the objective lens

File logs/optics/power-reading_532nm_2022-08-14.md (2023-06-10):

---
date: 2022-08-14
description: 'Laser power readings throughout the beampath'
measured by:
- David Curie
laser:
    - model: 'Verdi-5W'
    - serial: 'V5-G5403'
    - manufacture date: 'Dec-2004'
    - wavelength: 532
measurement:
    - device: 'Thorlabs PM101'
    - model: 'M00702598'
    - serial: '210608107'
    - calibration date: '2021-05-19'
    - mode: 'Mean over 4000 samples'
comments: 'Realigned fiber into laser on 2022-08-14'
---

The measurements from Aug 08 suggested an improper alignment into the fiber.

I realigned the objective and adjusted the coupling to the fiber until I
reached the maximum laser throughput as measured by the power meter. I then
quantified the amount of power present at each optical checkpoint based on a
set power of 0.01 W as declared on the laser power supply.

| Location                        | Measured Power (mW) |
|---------------------------------|---------------------|
| After laser objective           | 10.5                |
| After fiber exit                | 6.1  ± 0.2          |
| After 50x microscope objective  | 1.5  ± 0.1          |
| After 100x microscope objective | 0.44 ± 0.03         |

# Notes

- It seems like there is still a significant loss of power from the fiber
  through the objectives

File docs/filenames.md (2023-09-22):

# File naming conventions

Filenames need many descriptors to be unambiguous and sortable. The
convention below outlines appropriate metadata to include in filenames
to group them logically and allow for easy filtering by subsequent
scripts. This convention is based on an [almost flat][flat] naming
scheme that assumes all data generated by all instruments will be dumped
or archived in a central location. This naming convention allows for
programmatic reorganization at a later time.

```
sample_location_identifier_meas-type_source_set-power_NDfilter_objective_date-time.WIP
```

Note that fields are separated by underscores and that any multi-word
settings or field contents are separated by dashes. The important rule
is that **spaces are not encouraged**. Fields may be abbreviated.

| Field        | Value                                                                                               |
|--------------|-----------------------------------------------------------------------------------------------------|
| `sample`     | An abbreviated sample name, maintained in a separate database                                       |
| `location`   | An approximate location of where you are on the sample                                              |
| `identifier` | A way to identify which flake or region you are collecting                                          |
| `meas-type`  | Measurement type (confocal, external spectrum, AFM, SNOM) and whether in reflection or transmission |
| `source`     | Illumination (lasers expressed in nm, LED expressed by band)                                        |
| `set`-power  | (Necessary for Verdi only) Reading on laser power supply                                            |
| `NDfilter`   | (Necessary for Verdi only) Filter in place before fiber                                             |
| `objective`  | Microscope objective, identified by magnification                                                   |
| `date-time`  | YYYYMMDD-HHMM / YYYYMMDD-HHMMSS / YYYY-MM-DD-HH-MM where HH is in 24hr format                       |

The explicit presence of the `date` and `time` in the filename is to
differentiate between multiple acquisitions taken under the same
parameters. Both _ScanCtrlSpectroscopyPlus_ and _WinSpec_ provide an
option to auto-increment numbers at the end of a file when performing
sequential measurements, which is their attempt at maintaining globally
unique filenames. This method fails when you repeat an identical
measurement after opening a new program session or revisit a previous
sample to reacquire data, but is an appropriate stand-in for cases when
you can't programmatically assign a filename based on the current date
and time.

Given that the metadata in the files already contain the date and time,
users may opt to discard these fields at their discretion or when the
file has been appropriately bundled, archived, or otherwise uniquely
identified. If present, the date should be expressed in ISO 8601
standard, with optional dashes allowed between `YYYY-MM-DD` and
`HH-MM-SS`.

This project enforces no strict folder hierarchy for how data should be
organized after acquisition, as we expect users to maintain their own
data in whatever ways make sense to them. The guidelines herein ensure
that data generated from scripts in this can be deciphered by end-users
and manipulated by other scripts in this project.

## Examples

```
hBN-10_loc1A_flake01_conf-r_532nm_080mW_ND10A_obj50x_20230615-1324.WIP
Si-pillars_loc2B-2-7_nozzle_exts-r_405nm_obj50x_20230527-1712.WIP
```

| Field        | Example                   | Description                                         |
|--------------|---------------------------|-----------------------------------------------------|
| `sample`     | hBN-10                    | hBN made with Boron-10                              |
| `sample`     | Si-pillars                | hBN on nanopillars etched onto a Si substrate       |
| `location`   | loc1A                     | (Sample was partitioned into grids) view of grid 1A |
| `location`   | loc2B-2-7                 | Grid 2B, row 2, column 7                            |
| `identifier` | flake01                   | Arbitrarily defined flake w/in field of view        |
| `identifier` | nozzle                    | Description of shape of flake                       |
| `meas-type`  | conf-r                    | Confocal acquisition (w/ APD) in reflection mode    |
| `meas-type`  | conf                      | Confocal acquisition (w/ APD) (assumed: reflection) |
| `meas-type`  | exts-r                    | (EXT)ernal image (S)pectrum, reflection             |
| `meas-type`  | exts                      | (EXT)ernal image (S)pectrum, assumed: reflection    |
| `meas-type`  | conf-t                    | Confocal in transmission mode                       |
| `meas-type`  | snom-r                    | SNOM in reflection mode                             |
| `meas-type`  | afm-c                     | AFM in contact mode                                 |
| `meas-type`  | afm-n                     | AFM in non-contact mode                             |
| `meas-type`  | afm-t                     | AFM in tapping mode                                 |
| `source`     | 532nm                     | Verdi 532 nm (accompany w/ power settings)          |
| `source`     | 405nm                     | 405 nm (no additional power settings needed)        |
| `source`     | LED-UV                    | LED lamp with peak emission in ultraviolet          |
| `set`-power  | 080mW                     | (pad w/ leading zeros)                              |
| `NDfilter`   | f-ND10A                   | Name of neutral density filter before fiber         |
| `NDfilter`   | f-ND0                     | Explicitly state that no ND filter is in place      |
| `objective`  | obj-50x                   | 50x objective                                       |
| `date-time`  | 2023-06-15-16-28          | June 15, 2023 at 4:28 PM local time                 |
| `date-time`  | 20230615-1628             | June 15, 2023 at 4:28 PM local time                 |
| `date-time`  | 2023‐06‐15T14:28:39−07:00 | 2023-06-15 at 21:28 UTC-7:00 (time zone)            |
| `date-time`  | 20230615T212839Z          | 2023-06-15 at 21:28 UTC time (Zulu)                 |

In cases where the `location` and `identifier` are not known or easily
determined before acquisition, a description of the flake by shape or
acquisition sequence may suffice as descriptors.

## Motivation

The formula to describe your file should look something like this:

```
short-description_acquisition-type_settings_timestamp.WIP`
```

When collecting data directly from the WITec AlphaSNOM, aim to describe
the above fields in as succinct a manner as possible.

The `settings` field in the convention above is a placeholder for many
potential deviations that may depend on the specific acquisition. The
parameters that belong here are acquisition parameters that are not
already included in the file metadata.

See also:
- [File naming conventions](https://datamanagement.hms.harvard.edu/plan-design/file-naming-conventions)
- [Axiom Data Science](https://www.axiomdatascience.com/best-practices/DataManagementIntro.html)

[flat]: https://github.com/mitcommlab/Coding-Documentation/blob/master/File-Structure-Case-Studies.md#case-study-1-almost-flat

### Confocal image

A confocal image is fundamentally a series of measurements acquired at a
2D grid of coordinates. The shape and size of the grid is already stored
in the `.WIP` file, along with other parameters like the exposure
duration and date.

The experimental setup requires manual tweaks outside the scope of
_ScanCtrlSpectroscopy_, such as the laser power and choice of microscope
objective. This convention recommends describing these settings as a
sequence of how they are set, tracing from the source to the sample.

For instance, `settings` might be expanded in a confocal measurement to
include the following slug:

```
...wavelength_set-power_NDfilter_objective...
```

where it is assumed the setup is known and characterized based on these
parameters. In Stevenson 6517, the 532 nm Verdi laser is directed
through a neutral density (ND) filter and into a fiber, where it is
assumed to be focused onto the sample. These settings allow us to look
up the measured power at the sample and determine the actual power at
the sample. The additional presence of a date field allows us to look
back at any previously characterized setup if we make changes to the
optics assembly and log them appropriately by date..

Stevenson 6517 also contains an additional 405 nm diode laser, but this
is coupled directly into a fiber and does not have any adjustments that
can be made. Such a `settings` slug might look like this:

```
...wavelength_objective...
```

### External image spectrum

The following rule adopts convention 2 outlined near the end of [WITec
data formats](witec_formats.md) in that `.SPE` and `.WIP` files are
maintained as separate files complete with their own metadata.

If collecting an external image spectrum, the external WinSpec process
will create an additional file that stores the spectra outside of the
`.WIP` file. This file is strongly coupled to the parent
_ScanCtrlSpectroscopy_ process that called it, so the convention aims to
keep these files sorted together by using the same filename.

```
sample_location_acquisition-type_settings_date.SPE`
```

The metadata in the `.SPE` file contains many fields, such as
information about the grating and its position, the exposure time,
whether each spectrum was subtracted from a known background file, and
if any averaging was performed on the spectra. These would be redundant
fields to include in the filename, but sometimes it is helpful to
include these in the `settings` field if only because it helps
differentiate multiple acquisitions collected within the scope of a
specific investigation.

The relevant consideration is that the `settings` field be identical
between files. If there are additional tweaks to the setup that are made
present in an external image spectrum that are not contained in the
metadata of the `.SPE` or `.WIP` file, or additional and redundant descriptors are
deliberately included the settings to aid in mental differentiation,
they belong at the end of the `settings` field. Aim to include
abbreviated `keyword-value` fields separated by additional underscores
on either side.

## Additional processing

After data is collected from various instruments, you might make use of
scripts in this project to combine `.SPE` and `.WIP` files into one
`.hdf5` file for better packaging. The metadata in the `.WIP` and `.SPE`
filenames can and should be added to an appropriate (newly created)
metadata field in the `.hdf5` file. After this is done, some of the
descriptors in the filename may be safely removed if desired, but the
**original source data should remain intact**.

You may choose to keep these combined `.hdf5` files in separate folders
based on logical groupings. In cases where the folder structure contains
information present in the filename, you may also discard the filename
descriptor that duplicates this information.

```bash
mv sample_conf-r_settings_date.hdf5 user/sample/confocal/settings.hdf5
```

Some suggestions below outline potential avenues for data maintenance.

### Additional sorting

Be aware that projects exist that can help manage, search, and access
data by its parameters space such that strict folder management is not
necessary. Using a tag-based indexing instead of a folder-based indexing
may appear messier for human inspection, but it provides quicker search
results for large file sets and allows for groupings that don't fit
cleanly into folders.

For example, in a folder-based structure all of Justin's measurements
might be under a `Justin` user folder, and all of Britney's measurements
might be under a `Britney` user folder. If Justin and Britney
collaborate on the same project, however, they need to decide whose
folder the data belongs under. Maybe they make a new folder
`Britney+Justin`. Two years later, Justin wants to grab all the data he
is responsible for and make a permanent backup of it. Hopefully he
remembers to also grab the `Britney+Justin` folder and any other
collaboration folders.

In a tag-based structure, Justin tags any files that belong to him with
a metadata tag, say, `owner: Justin`. Files can have multiple owners.
They can also have tags pertaining to who performed the measurement.
When Justin wants to make his archive, he can simply ask a program to
find all files with `owner: Justin` somewhere in their metadata and dump
those into `Justin-archive.zip`

Projects like [signac](https://github.com/glotzerlab/signac) attempt to
make this latter organization principle easier to implement in Python.
Users are expected to lump all data and their associated metadata into a
single project folder. Files are given a hashable index as a filename
for quicker machine recall, but this then obscures human browsing of the
file structure. Instead, individual files are expected to be retrieved
through scripts to downselect members of a project folder based on
user-defined filters. At any time, users can use a script to auto-sort
data into meaningful folder structures based on an appropriate filter
criteria. Each sorting is called a _view_. These views can be undone and
refined at any time as the project becomes more nuanced in scope.

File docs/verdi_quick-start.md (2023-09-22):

# Quick Start Guide - Coherent Verdi V-5 Laser

For use in Stevenson 6517. Additional notes on reverse side.

## Turn-On (Cold Start)

1. Ensure the keyswitch is in the STANDBY position.
2. Set the power switch on the power supply rear panel to ON. The AC power and
   LASER EMISSION indicators will light. The power supply display will then
   indicate "System warming up".
3. Turn on the chiller. Verify there are no cooling line connection leaks at the
   Verdi riser/heat sink and at the chiller.
4. Verify the chiller water temperature is set to approximately 20ºC. Adjust 
   the temperature setpoint as required.
5. Set the output power to the desired level using the POWER ADJUST knob. The
   output power can be adjusted to 0.01 watts to facilitate beam alignment.
6. Allow 30 minutes for the heaters and thermo-electric coolers (TECs) to
   achieve operating temperature. The status of all servos can be viewed by
   scrolling to the Servo Status screen. Once this process is complete, the
   system is now ready for key on.
7. Ensure the laser output is blocked or directed at an intended target.
   **Ensure all personnel in the area are wearing laser safety glasses.** Turn the
   keyswitch on the power supply front panel to ON.
8. Open the shutter by pressing the SHUTTER OPEN pushbottn on the power supply
   front panel.
9. Laser light will emit from the laser head after the current ramp-up.

## Daily Turn-On (Warm Start)

A warm-start can be performed when the Verdi power supply rear panel power
switch has been on for more than 30 minutes (laser in standby).

1. Verify there are no cooling line leaks at the Verdi riser/heat sink and at
   the chiller. Verify the chiller water temperature is set to 20ºC. Adjust the
   setpoint temperature as required.
2. The LASER EMISSION indicator should be on. Ensure the laser output is blocked
   or directed at an intended target. Turn the keyswitch on the power supply
   front panel to ON.
3. Open the shutter by pressing the SHUTTER OPEN pushbottn on the power supply
   front panel.
4. Laser light will emit from the laser head after the current ramp-up.

## Daily Turn-Off (Standby)

When the Verdi is being used on a daily basis, turn-off consists of turning the
keyswitch to the STANDBY position. This shuts off the laser diodes and places
the Verdi in standby. This method avoids the heater ramp-up cycle described in
the "Turn-On (Cold Start)" section. The system water chiller should be left on
during short-term shut downs.

> Do not turn the power switch on the power supply rear pane to the OFF
> position.

## Complete Shut Down

1. Turn the keyswitch power supply front panel to STANDBY.
2. Access and select the LBO Settings submenu. Press the MENU SELECT pushbotton
   to start the LBO cool-down cycle.**This cycle takes approximately 30
   minutes.**
3. During the cool-down cycle, the LBO temperature can be monitored from the
   main screen or the LBO Settings submenu. When the LBO temperature decreases
   below 30ºC, tun the AC power switch on the power supply rear panel to the OFF
   position.
4. Turn off the chiller.

> These operating instructions are borrowed from a Verdi V-8 laser. An
> unofficial copy of the Verdi V-8/V-10 diode pumped laser manual can be found
> at
> <https://vdocuments.net/operators-manual-verdi-v-8v-10-diode-pumped-lasers.html>.

# Operating States

+---------+-------------------------------------+--------------------------------------------------------------+
| State   | Switch Position                     | Status                                                       |
+=========|=====================================|==============================================================+
| OFF     | - Power Switch (rear panel): ON     | All functions off except LBO CPU until cool-down is complete |
|         | - All other switches : Any position |                                                              |
+---------+-------------------------------------+--------------------------------------------------------------+
| STANDBY | - Power Switch (rear panel): ON     | - Laser diodes off                                           |
|         | - Keywitch: STANDBY                 | - Vanadate temperature servo off                             |
|         |                                     | - LBO temperature servo on                                   |
|         |                                     | - Etalon temperature servo on                                |
+---------+-------------------------------------+--------------------------------------------------------------+
| ON      | - Power Switch (rear panel): ON     | - Laser diodes on                                            |
|         | - Keywitch: ON                      | - Vanadate temperature servo on                              |
|         |                                     | - LBO temperature servo on                                   |
|         |                                     | - Etalon temperature servo on                                |
+---------+-------------------------------------+--------------------------------------------------------------+

## Other notes

- The water in the chiller should be changed out approximately every 6 months.
  Use distilled water.
- Maintain a weekly log of the diode current (read from the front screen on the
  power supply) vs. output power. If the diode current increases 10% or more 
  over the initial installation value (or current baseline value) to achieve the
  same output power, use the LBO Optimization menu as outlined in the manual.
- The digital version of this document lives in the accompanying WiTEC
  microscope computer under `Documents/Manuals/Verdi`

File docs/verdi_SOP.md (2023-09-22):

---
title-meta: "Standard Operating Procedures for Stevenson 6517"
author-meta: David Curie
geometry:
- margin=1in
---

# SOP - Coherent Verdi V-5 Laser - Stevenson 6517

**The American National Standards Institute (ANSI) Standard for Safe Use of
Lasers requires that Standard Operating Procedures (SOP) be written and
approved for Class 3B and 4 lasers or laser systems.**

> This SOP pertains to one of two Verdi lasers located in Stevenson 6517. This
Verdi-V5 is located near the lab entrance and is enclosed in a shielded opaque
box under normal operation. Output light is coupled into a fiber that runs
directly to an upright confocal microscope. While the laser is classified as
a Class IV laser according to its manufacturer, the output light from the
microscope objective does not exceed 5 mW under typical operation with the
surrounding enclosure intact.

## System description

|                                          |                                                    |
|------------------------------------------|----------------------------------------------------|
| Type of laser                            | Diode-pumped, frequency-doubled Nd:YAG             |
| Manufacturer                             | Verdi                                              |
| Model                                    | Verdi-V5                                           |
| Serial Number                            | V5-G5403                                           |
| Classification                           | Class 4                                            |
| Wavelength                               | 532 nm                                             |
| Power                                    | variable, up to 5 W                                |
| Energy per pulse                         | N/A (continuous)                                   |
| Pulse duration                           | N/A (continuous)                                   |
| Repetition rate                          | N/A (continuous)                                   |
| Output beam diameter                     | 2.25 mm ± 10%                                      |
| Beam divergence                          | < 0.5 mrad                                         |
| Intended application                     | Excitation source for photoluminescence microscopy |
| Other system attributes not listed above | External water chiller required for use            |

## Hazards

### Beam hazards

None under typical use.

Alignment procedures dictate using low power (0.01 W) for beam
alignment---in which case no additional beam hazards are present.

### Non-beam hazards

#### Eye

Avoid eye exposure to direct or scattered radiation within the
enclosure box. Avoid eye exposure to the end of the output fiber. Do not
use optical aids to look at the illuminated sample in the microscope.

#### Skin

None under typical use.

#### Laser-generated air contaminants (LGAC)

None under typical use.

#### Scattered radiation

None under typical use.

#### Electrical

None under typical use.

#### Other

Potential for water leaks from coolant system.

Ensure that there is sufficient water in the external chiller and that there
are no leaks during chiller operation. Spilled water presents an electrical
hazard to nearby power supplies and a slip hazard to nearby operators.

Insufficient cooling of the laser will damage the diode. If leaks are detected,
start the shutdown procedure immediately.

## Control measures

### Laser protective eyewear type(s) and requirements for use

During alignment, wear appropriate safety goggles that specifically cover
532 nm emission with OD \> 4. Remove jewelry (e.g. watches, rings, earrings) to
mitigate scattering risks. Use an alignment card to view the beam.

### Laser control area

Under normal operation, the laser is enclosed in an opaque box that mitigates
scattering hazards. Light is coupled to a fiber that runs directly to
a confocal microscope. The total power of the focused laser light through the
microscope objectives is nominally a few milliwatts, and varies slightly depending on
specific microscope objectives and laser operation power.

If alignment to the output fiber is necessary, the enclosure box may be
disassembled, in which case the system should be treated like a class IV laser
that is capable of producing 5W laser light. Direct beam exposure at high power
presents a fire hazard to flammable fabrics worn by users, burn hazards for
unintentional skin contact, and eye hazards for **direct and scattered**
radiation.

Protocols in this SOP dictate the laser be used in low-power mode (0.01 W)
during alignment.

### Entryway controls

Ensure the laser indicator light outside of the lab entrance is illuminated
whenever the laser is on. The switch to control this indicator light is the
right-most switch on the row of light switches near the entryway door and is
labeled "Laser".

### Reference manual

These operating instructions are borrowed from a Verdi V-8 laser. An
unofficial copy of the Verdi V-8/V-10 diode-pumped laser manual can be found
at
<https://vdocuments.net/operators-manual-verdi-v-8v-10-diode-pumped-lasers.html>.

An additional copy of the above referenced manual, along with manuals for
accompanying equipment for this laser, can be found at
<https://github.com/Stevenson6517/Witec> under the `docs` folder.

This document can be edited at
<https://github.com/Stevenson6517/Witec/blob/main/docs/verdi_SOP.md>.

<!-- ...and generated as a PDF with the following command: -->

<!-- ```bash -->
<!-- pandoc -o verdi_SOP.pdf verdi_SOP.md -->
<!-- ``` -->

### Procedures for safe alignment

Adjust the output on the power supply panel to its lowest setting (0.01 W).
Remove any jewelry and reflective articles of clothing and tie back long hair.
Remove all persons from the lab except for those actively involved in
alignment. Each active participant should wear laser safety goggles appropriate
for the laser (OD \> 4 at 532 nm). Work with the room lights on if possible.

Remove the side panel of the lab-made laser enclosure, taking care not to pinch
the optical fiber or water cooled lines that exit through a notch in the panel.
Open the laser shutter and begin alignment. Use an alignment card to view the
beam.

After alignment into the output fiber is complete, reassemble the laser
enclosure system.

### Turn-On (Cold Start)

1. Ensure the keyswitch is in the STANDBY position.
2. Set the power switch on the power supply rear panel to ON. The AC power and
   LASER EMISSION indicators will light. The power supply display will then
   indicate "System warming up".
3. Turn on the chiller. Verify there are no cooling line connection leaks at the
   Verdi riser/heat sink and at the chiller.
4. Verify the chiller water temperature is set to approximately 20ºC. Adjust 
   the temperature setpoint as required.
5. Set the output power to the desired level using the POWER ADJUST knob. The
   output power can be adjusted to 0.01 watts to facilitate beam alignment.
6. Allow 30 minutes for the heaters and thermo-electric coolers (TECs) to
   achieve operating temperature. The status of all servos can be viewed by
   scrolling to the Servo Status screen. Once this process is complete, the
   system is now ready for key on.
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

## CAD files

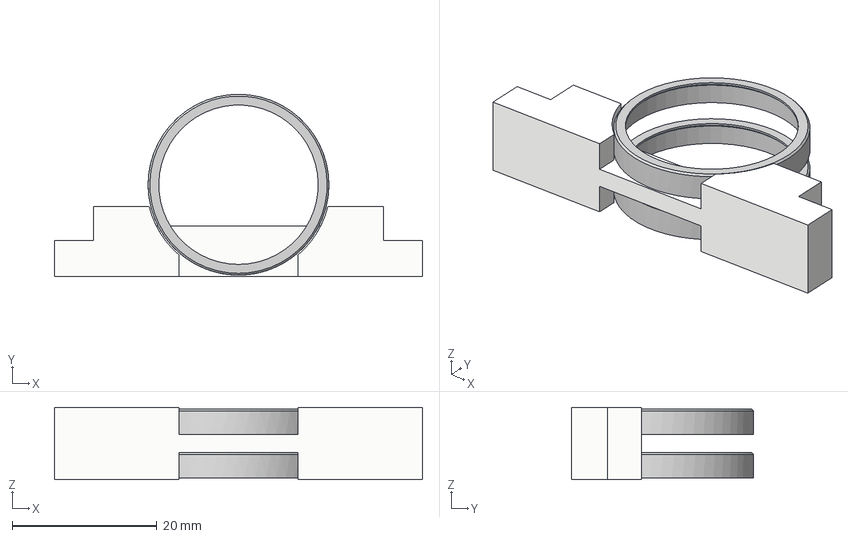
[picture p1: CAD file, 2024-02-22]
logs/optics/media/assembly_filter-holder.step
50.8 x 25.2 x 10.0 mm
25.0mm-X-3.5mm_filter-case x 2
line-filter_holder_v2

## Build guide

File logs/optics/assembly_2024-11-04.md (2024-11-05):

---
date: Mon Nov 04 19:00:00 CST 2024
author:
- David Curie
- Ryan Kowalski
---

# Photoluminescence fiber collection

The top of the WITec microscope comes configured from the manufacturer to
collect the photoluminescence signal onto the core of a multi-mode fiber. The
discrimination afforded by the small core diameter of the fiber acts as
a pinhole detector, enforcing a key requirement of confocal microscopy.

The existing fiber positioner is suited for moving the core of the input fiber
into the fixed path of the reflected PL signal. Once aligned, the output of the
multi-mode fiber can be directed to a number of instruments without requiring
fiber realignment.

## Problem

The existing fiber positioner and end-point detectors that accompany the WITec
measurement depend on fibers with SMA connectors. Explicitly, these detectors
are the Princeton Instruments Acton 300i spectrometer and the APD
photon-counting module integrated underneath the WITec microscope stage.

We wish to integrate more detectors into this setup.

We have a fiber-coupled external Hanbury Brown–Twiss (HBT) interferometer
capable of single-photon characterization. This uses a custom fiber with an
integrated beam splitter, whose single input and double output fibers use FC/PC
connectors. The fiber input is suitable for cases where we want permanent and
dedicated input alignment to the interferometer while maintaining configurable
downstream components in the optical pathway without significant re-alignment
costs.

The FC/PC input fiber to the HBT is incompatible with the WITec SMA fiber
positioner.

The lowest-cost solutions involve using a single SMA-to-FC/PC adapter or
replacing the custom fiber-based beam splitter for one with an SMA input
connector. Each of these solutions would also require disconnecting the fiber
at the microscope connection instead of at the detector connection. This means
that switching between a spectrometer measurement (SMA fiber) and
a complementary single-photon measurement (FC/PC fiber) would require
re-alignment onto the respective fiber core. This impedes rapid studies of
correlated measurements on a single sample.

## Solution

We seek a modification to the fiber coupling atop the WITec microscope that
would accept two types of fibers with an easily switchable configuration. The
original SMA fiber would continue to the spectrometer or photon counting
module, and the FC/PC fiber would incorporate the HBT interferometer.

The target of our modification is summarized by the mock-up in the figure
below.

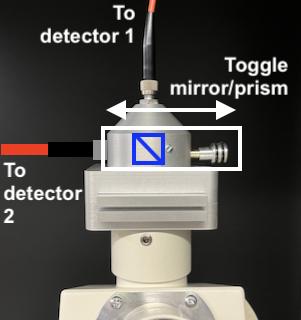
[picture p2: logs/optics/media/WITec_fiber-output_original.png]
Original WITec multimode fiber collection with an overlay of representative desired functionality Original PL fiber collection mechanism


The essential criterion is that our modifications should allow for reversible
and repeatable reconfiguration between the two fiber ports. As a secondary
consideration, we want the reconfiguration to be programmable.

Based on the original configuration shown below, we decided the best course of
action was to extend the infinity space---the region between the
infinity-corrected microscope objective (5) and the tube lens (7)---to make
room for us to implement a custom diverter atop the microscope.

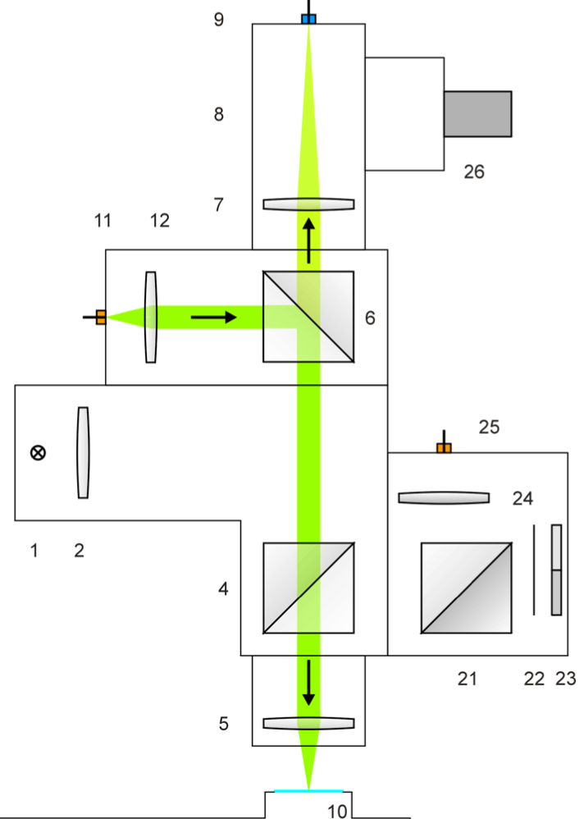
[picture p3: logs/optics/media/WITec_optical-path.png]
Original WITec optical path Original WITec confocal configuration


### Modifications

The schematic figure below illustrates the top of the WITec microscope, which
holds a prism diverter assembly capable of directing the optical path to the
binocular lens or top fiber coupler. The prism diverter assembly is aligned to
its base by an aluminum alignment collar, held in place by a set screw under
the push-rod prism diverter (3).

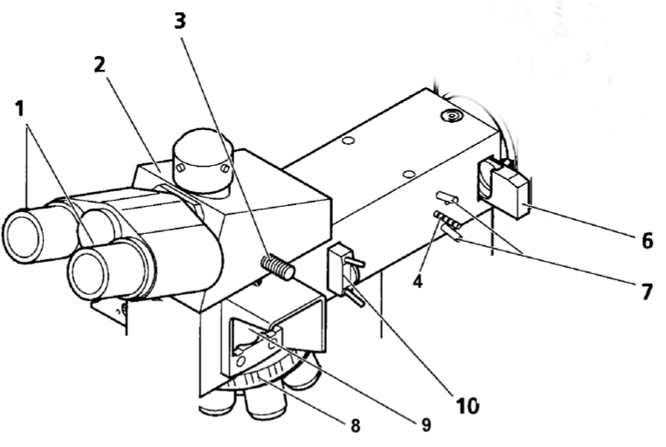
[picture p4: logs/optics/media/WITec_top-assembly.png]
WITec top microscope assembly


The picture below shows the original tube lens mounted under the prism
assembly, with the aluminum alignment collar temporarily removed for visual
clarity. The tube lens is screwed tightly into the bottom of the prism
assembly. 

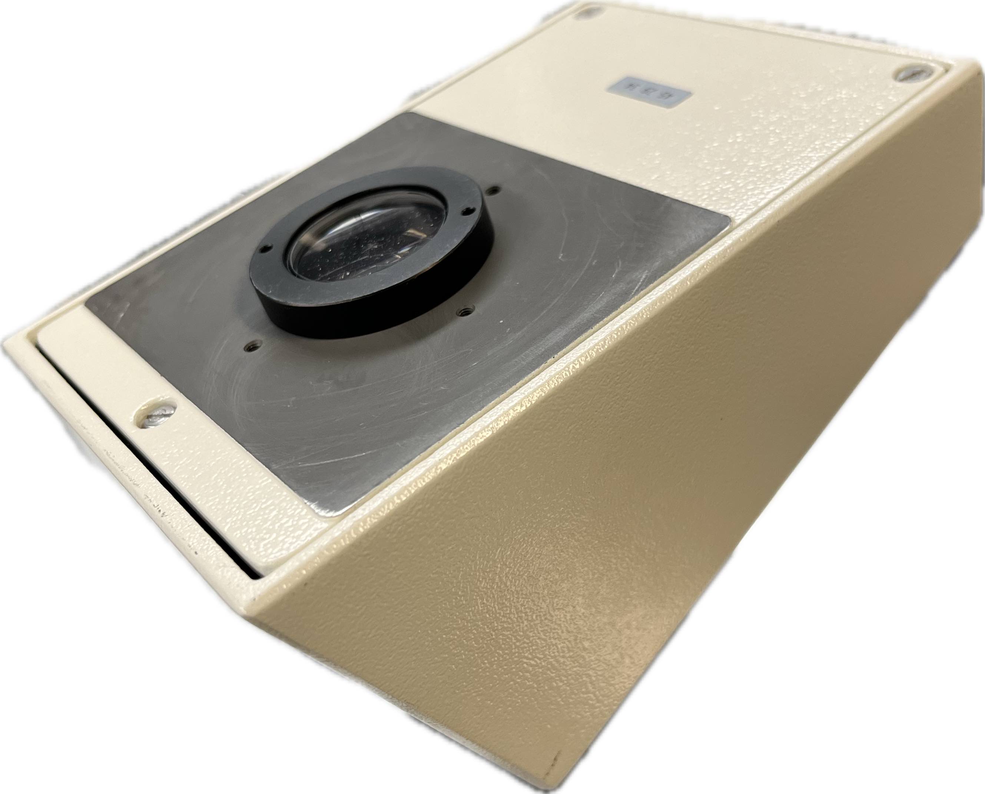
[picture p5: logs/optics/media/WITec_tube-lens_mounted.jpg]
Tube lens mounted to the top prism diverter assembly Original tube lens assembly


We removed the tube lens, re-secured the alignment collar, and reassembled the
microscope. We then replaced the top fiber positioner with a cage assembly
capable of directing the collimated light exiting the top of the microscope
into one of two arms. In each arm, the light is focused onto the core of
a fiber. The cage contains a longer focal length tube lens and a mechanised
diverter to select between collection arms.

To secure this cage to the top of the microscope, we made a custom adapter
plate to replace the fiber positioner and provide the base for the upright
cage. The mechanical arm for the diverter mirror is mounted to a metal plate
customized to fit inside the cage rods. We elevated this support plate above
the adapter plate to allow for tunable spectral filtering. The longer focal
length tube lens was necessary in this cage to allow for the diverter arm to
swing in and out of position. The diverter mirror can be controlled by
software, but we currently use a button switch to toggle between the two states
manually.

The original 163 mm tube lens was moved to the eyepiece side of the top prism
diverter. We removed the binocular assembly and 3D printed a custom holder to
fix the video camera at the focal length of the tube lens.

### Summary of components

Machined parts

- [`logs/optics/media/WITec_adapter_plate.pdf`](media/WITec_adapter_plate.pdf)
- [`logs/optics/media/WITec_support_plate.pdf`](media/WITec_support_plate.pdf)

3D printed parts

- [`logs/optics/media/WITec_binocular_adapter.pdf`](media/WITec_binocular_adapter.pdf)
    - Made to hold the original WITec tube lens
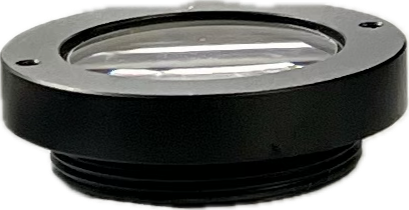
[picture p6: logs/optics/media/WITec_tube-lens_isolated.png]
Original WITec tube lens (f = 163 mm)
    - 

Purchased parts

| Part Description                                                    | Thorlabs Part Number | Quantity |
|---------------------------------------------------------------------|----------------------|----------|
| Cage Assembly Rod, 12" Long, Ø6 mm                                  | ER12                 | 4        |
| Cage Assembly Rod, 2" Long, Ø6 mm                                   | ER2-P4               | 2        |
| Cage Assembly Rod, 3" Long, Ø6 mm, 4 Pack                           | ER3-P4               | 2        |
| XYZ Translation Mount for Ø1" Optics, 1/4"-20 Taps                  | CXYZ1A               | 3        |
| N-BK7 Plano-Convex Lens, Ø1", f = 175 mm, AR Coating: 400 - 1100 nm | LA1229-AB            | 1        |
| Motorized Filter Flip Mount with Ø1" Optic Holder, 8-32 Tap         | MFF101               | 1        |
| 60 mm to 60 mm Cage System Right-Angle Adapter                      | LCP60                | 1        |
| Ø1" FC/PC Fiber Adapter Plate Without Threads, Wide Key (2.2 mm)    | S1FC                 | 1        |
| Ø1" SMA Fiber Adapter Plate Without Threads                         | S1SMA                | 1        |
| Pivoting, Quick-Release, Ø1" Optic Mount for 30 mm Cage System      | CP360Q               | 2        |

## Results

The final assembly appears below.

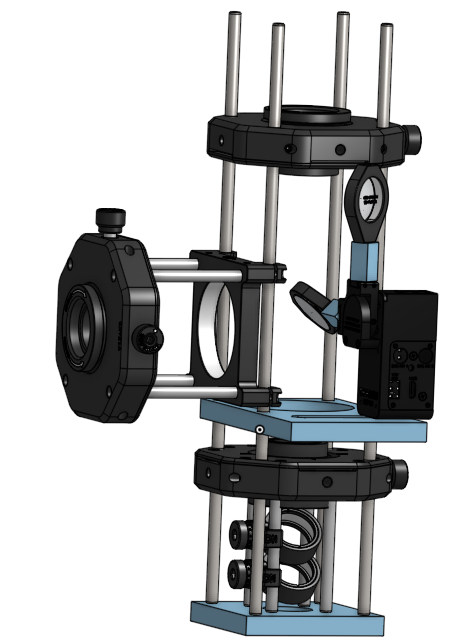
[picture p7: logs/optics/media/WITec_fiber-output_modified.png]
Modified WITec multimode fiber collection with switchable configuration Cage rods mounted to the top of the WITec microscope in a T configuration


This new configuration allows for single-photon detection and rapid evaluation
of spectra in one microscope, under the same stage coordinates, and in a nearly
seamless switchable configuration.

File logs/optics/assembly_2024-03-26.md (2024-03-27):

---
date: Tue Mar 26 19:00:00 CDT 2024
author: David Curie
---

# Microscope objectives

The WITec microscope currently has the following infinity-corrected objectives
configured for use.

| Label                     | Magnification | NA   | Working Distance | Parfocal length | Threading   |
|---------------------------|---------------|------|------------------|-----------------|-------------|
| Nikon LU PLAN FLUOR EPI   | 50x           | 0.80 | 1.0 mm           | 60 mm           | M25         |
| Zeiss EC Epiplan-Neofluar | 100x          | 0.90 | 1.0 mm           | 45 mm           | M27x0.75-40 |

The mismatch in model of lenses used in the same optical setup means that the
magnification inscribed on the lens is not representative of the real
magnification of the image. This is of little concern to us because the
ScanCtrlSpectroscopyPlus software is capable of calibrating the image pixels in
the eyepiece camera to the known displacement of piezoelectric stages under
the objective.

See also: 

- [Magnification in infinity optics][infinity-optics]
- [Infinity optical systems][infinity-systems]

[infinity-optics]: https://evidentscientific.com/en/microscope-resource/tutorials/infinityoptics/magnification
[infinity-systems]: https://www.microscopyu.com/microscopy-basics/infinity-optical-systems

## Existing problem

The objective turret on the WITec microscope accepts M27 threaded objectives,
so the Nikon lenses must be mounted with an adapter collar. The difference in
parfocal length and the presence of the adapter collar in the Nikon lens mean
that rotating between different microscope objectives mandates significant
refocusing on the stage. Furthermore, the difference in height required to
obtain stage focus between objectives is geometrically infeasible when both
lenses are configured in the objective turret because the lengthier Nikon lens
hits the stage when we lower the microscope to focus with the 100x Zeiss
objective.

We have previously avoided this second problem by placing our sample on
a separate elevated mini stage when using the 100x Zeiss objective. This
required us to commit to one objective per investigation, as moving the sample
on or off this mini stage resets our absolute stage coordinates and prevents
repeatable investigations.

## New collar adapter

We have newly solved our second problem above to allow for both objectives to
remain installed with no physical geometric obstruction between focus points.
Our new solution extends the 100x Zeiss objective by a nominal length to put
its effective parfocal length on par with those from Nikon lenses. This
solution eliminates the need to move the sample off or onto a mini stage
when switching objectives.

I deduced the necessary extension distance by recording the difference in stage
coordinates between a focused image under each objective. The exact focus point
in each case was determined as the distance that resulted in the smallest spot
size of the collimated Verdi laser beam on a flat reflective sample.

The stage coordinates in the PIMikroMove software do not appear to be
calibrated to their displayed units in mm. Thus, after recording the difference
in stage coordinates between objectives, I also measured the difference in
stage coordinates between a sample focused on the WITec stage and a sample
focused on the elevated mini stage, whose real distance I could measure
accurately with calipers. After normalizing the stage coordinates to real
units, the real translated distance between objectives was 22.757 mm.

| Objective                 | Collar length |
|---------------------------|---------------|
| Zeiss EC Epiplan-Neofluar | 22.757 mm     |

A representative schematic of the existing Zeiss objective appears below. The
collar was designed to fit between this objective and the stock objective
turret in the WITec microscope with the collar length specified above.

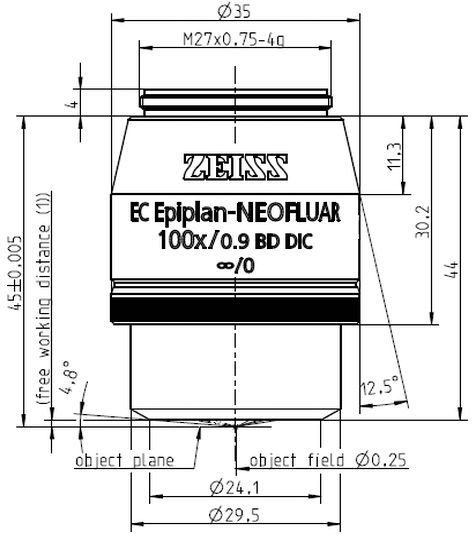
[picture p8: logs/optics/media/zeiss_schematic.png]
Representative Zeiss objective. Figure from <https://www.micro-shop.zeiss.com/en/us/shop/objectives/422392-9961-000/Objective-EC-Epiplan-Neofluar-100x-0.90-BD-DIC-M27#> Zeiss EC Epiplan-Neofluar dimensions


> If replicating this collar in Stevenson 6517, have the machinist confirm
dimensions of the threads before machining.

### Observations and results

After installing the collar adapter on the Zeiss 100x objective, the difference
in optimal focus between the two objectives is within 1 mm. This difference is
attributed to machining tolerances in the brass collar and the degree to which
the collar is tightened into the objective turret.

Although the magnification should not be affected in an infinity-corrected
lens, we re-calibrated the scale on the xy-piezoelectric stage coordinates in
the ScanCtrlSpectroscopyPlus VideoControl module. Look for the scale settings
along the lines `100x 0.9NA with collar`.

As a secondary observation, we note that the center positions of each objective
are not exactly concentric. That is, rotating the objective turret between
lenses results in a laser spot whose focused position is approximately 10 µm
offset from the previous configuration. The direction and magnitude of this
displacement is unique to the specific two turret slots that the objectives are
mounted in. This offset also appears to depend on how tightly each objective is
mounted into the turret.

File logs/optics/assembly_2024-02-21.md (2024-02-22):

---
date: Wed Feb 21 19:00:00 CST 2024
author: David Curie
---

# WITec laser bay

The laser bay in the WITec AlphaSNOM receives a fiber-coupled laser beam and
collimates it onto a beam-splitter, where it enters the infinity-space of an
upright confocal microscope.

The original laser bay from the WITec AlphaSNOM 300 is configured to receive
a filter assembly to apply corrections to the beam path before the laser
reaches the beam splitter. Our model does not come equipped with this optional
configuration.

This guide outlines the modifications we made to the original configuration to
support our own custom filtering.

## Laser line filter

The spectra observed from samples illuminated by the Verdi laser in the WITec
microscope are known to have strong broadband fluorescence near the laser line
(532 nm). This fluorescence impedes our ability to measure meaningful
photoluminescence from the sample. We determined the source of this
fluorescence to originate in the single-mode fiber carrying the 532 nm laser.
It is unclear if this fluorescence is from the fiber cladding or from a defect
within the core of the fiber, but this phenomenon is repeatable for at least
two different single-mode fibers.

Alex Klapowitz 3D printed a plastic holder at the Wondry with dimensions
specified in [`assembly_filter-holder.step`](media/assembly_filter-holder.step)
that holds a laser line filter normal to the beam path.

This filter needs to be updated whenever the laser source is updated.

## Change the filter in the laser bay

The instructions below show you how to access the 3D-printed filter holder.

### 1. Remove top microscope assembly

- Loosen the three locking screws on the top microscope collar and remove the
  top microscope assembly.

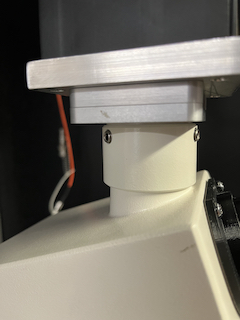
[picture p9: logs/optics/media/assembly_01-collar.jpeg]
Locking screws securing top microscope assembly inside a steel collar. Top microscope assembly


### 2. Remove diverter prism

- Remove the camera from the eyepiece above the diverter prism.
- Loosen the set screw below the diverter prism.

Set screw below prism assembly mounted into the top of the laser bay Diverter prism set screw

- Tilt to lift off the diverter prism and set aside. The prism mates with the
  lower microscope body through an alignment collar fixed to the prism that
  sits inside a grove of the laser bay.

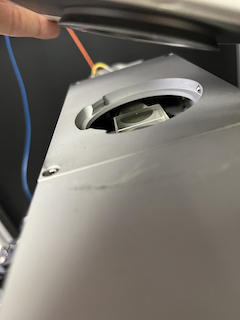
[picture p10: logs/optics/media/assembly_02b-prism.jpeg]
Lateral close up of mating mechanics outlining the required tilting motion to unseat the prism assembly Diverter prism locking mechanism


Axial view through the locking collar which is attached to the bottom of the prism assembly Bottom view of locking collar of diverter prism

### 3. Open laser assembly

- Remove the screws on the top corners of the laser assembly.

Laser bay with metal roof. Circular cutout in the middle receives the diverter prism assembly Laser bay roof held by 4 screws

Laser bay with metal roof removed. Laser filter sits in the back about halfway between the attached collimating optic and the beam splitter Exposed laser bay with roof removed

### 4. Reassemble

- Repeat instructions in reverse order for reassembly.
- Realign collection optics at the top of the microscope after reassembly.

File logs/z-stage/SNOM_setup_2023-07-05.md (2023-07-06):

SNOM\_setup\_2023-07-05

Wednesday, July 5, 2023

7:30 PM

Found box labeled "WITEC stuff" containing 9 cantilevers and 7 probes with apertures as well as 15 "practice tips."

-   Removed SNOM objective endcap by loosening tiny screw on the side

-   Attached practice cantilever to endcap by placing the two washers on top of each other (not an easy task), as per the image on page 115 of WITEC manual.

-   Re-attached endcap to SNOM objective

Collection CCD (below microscope)

-   ScanCtrl didn't seem to recognize it so I unplugged it and tested with a multimeter, which showed 29V DC. Plugged it back in and it worked after a small delay.

-   Z motor (controlling collection objective) appears to be on its way out and only sometimes responds to the handheld controller. X and Y motors function better but are slightly jerky at slow speeds.

-   Manual focus knob bypasses Z motor and allows for focusing. Was able to get an image of coverslip from below on ScanCtrl.

-   *Microscope* z-stage doesn't go down far enough to allow for focusing

    -   Was able to get the collection objective high enough to focus on the field stop by placing the coverslip on a 1" tall ring and feeding the collection objective through the hole.

>  
>
> 
>
>  
>
>

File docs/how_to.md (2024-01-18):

# How To Guides

## Standard Operating Procedures

- [Verdi V5 laser](verdi_SOP.pdf)

## Manuals

### WITec

- [WITec AlphaSNOM Operation Manual](manuals/Witec_Operation_Manual_SNOM092004.pdf)
- [WITec Project](manuals/WITec_Project.pdf)
- [ScanCtrlSpectroscopy](manuals/Witec_ScanCtrlSpectroscopyPlus.pdf)
- [High Resolution Optical Microscopy](manuals/Witec_Tutorial_High-Resolution-Microscopy.pdf)

### Princeton Instruments

- [Acton300i Spectrometer](manuals/Princeton-Instruments_SP-300i_Manual.pdf)
- [PIXIS CCD](manuals/Princeton-Instruments_PIXIS_100_datasheet-rebranded.pdf) (350--1050 nm)
- [VersArray System](manuals/Princeton-Instruments_VersArray-System_Manual.pdf) (800-1700 nm)
- [WinSpec32](manuals/Princeton-Instruments_WinSpec32_UserManual2.6.pdf)

### PI Micos

- [PI MikroMove](manuals/PI-micos_MikroMove_SM148E_UserManual.pdf)
- [Venus-2 serial commands](manuals/PI-micos_SMC-Pollux_Venus2_Longform_V2-3.pdf) (full)
- [Venus-2 serial commands](manuals/PI-micos_SMC-Pollux_Venus2_Shortform_V12.pdf) (abbreviated)
- [SMC Pollux Micro Controller](manuals/PI-micos_SMC-Pollux_Motion_Controllers.pdf)
- [ES100 Elevation Stage](manuals/PI-micos_ES100_ElevationStage.pdf)

### Coherent

- [Verdi-V5 Preinstallation Manual](manuals/Verdi_V2-V5-V6_Preinstallation.pdf)
- [Verdi-V5 Operation Manual](manuals/Verdi_V2-V5-V6_Manual.pdf)

### Schott

- [KL 1500 LCD](manuals/Schott_KL1500LCD_Manual.pdf) (white light illumination)

## How To 

### General

- [Properly name files](filenames.md)

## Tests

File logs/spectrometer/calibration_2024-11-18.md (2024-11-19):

---
date: Mon Nov 18 19:00:00 CST 2024
author: David Curie
measured by:
- David Curie
- Richarda Nieman
- Ryan Kowalski
subject: "Spectrometer calibration"
---

# Princeton Instruments Action 300i

The following gratings have been re-calibrated against the spectra from
a mercury lamp.

- Grating 1: 150 lines/mm
- Grating 2: 600 grooves/mm
- Grating 3: 1800 grooves/mm

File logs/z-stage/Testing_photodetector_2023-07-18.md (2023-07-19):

Testing\_photodetector\_2023-07-18

Tuesday, July 18, 2023

6:51 PM

Fabricated 2 aluminum setscrew mounts opposite existing knobs on SNOM objective to replace spring system. To translate in the x or y direction via the knobs, one knob must be twisted clockwise and its opposing knob must be twisted counterclockwise. \*Since there are fewer threads per inch on the new setscrews compared to the existing ones, the new setscrews must be screwed in and out at a slower rate while rotating their opposite setscrew to avoid compressing the stage.\*

Verdi power at fiber tip: ~4 mW, same as near-IR laser.

Green light not visible on CCD when coupled into SNOM tip input. No increase in T-B, L-R, or $\\Sigma$ values.

-   Rotated endcap 180 degrees. Still no signal or spot on cantilever/screen.

    -   Re-coupled IR laser. Still no signal.

-   "Focus of the beam deflection laser can be seen 50 um above the pyramid" -- manual

-   Turning adjustment screw T-B makes no difference

Either the beam isn't reaching the objective due to a missing/poorly aligned mirror or the photodetector is not working.

-   Upon closer inspection, there seems to be a mirror system that is missing in the microscope that would direct the feedback laser to the cantilever (see below image)

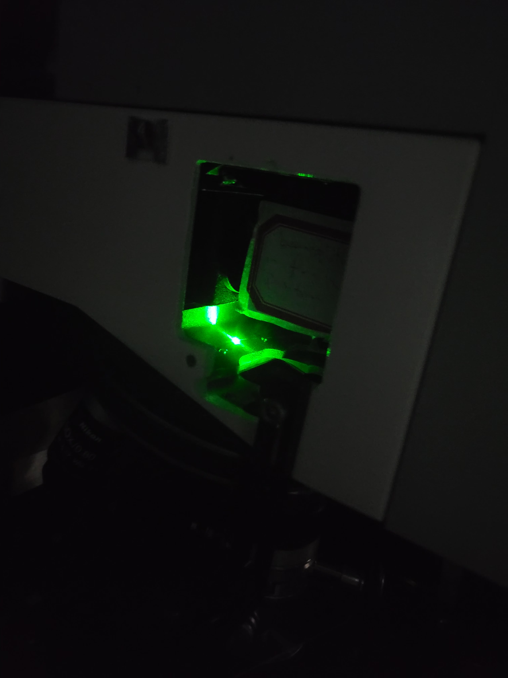
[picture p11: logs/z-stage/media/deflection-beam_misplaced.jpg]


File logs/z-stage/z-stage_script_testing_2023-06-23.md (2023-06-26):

z-stage\_script\_testing\_2023-06-23

Friday, June 23, 2023

2:40 PM

Windows 7 PC (HP)

-   Sent command "echo 1.0 1 nr &gt; COM7" to z-stage via cmd as administrator

    -   "access is denied"

    -   Changed COM7 to COM1 in device manager

        -   Didn't work

    -   Restarted computer

-   Sent command "1.0 1 nr" to pollux via PIMikroMove Command Entry -- didn't work

    -   Closed PIMikroMove -- no error, but no response

-   Sent command "HLP?"

    -   Listed following commands:

> &lt;&lt;\#4 query status word
>
> &lt;&lt;\#5 request motion status
>
> &lt;&lt;\#7 request controller ready status
>
> &lt;&lt;\#24 stop all axes
>
> &lt;&lt;\*IDN? Get Device Identification
>
> &lt;&lt;ACC {&lt;AxisID&gt; &lt;Acceleration&gt;}
>
> &lt;&lt;ACC? \[{&lt;AxisID&gt;}\] get closed-loop acceleration
>
> &lt;&lt;CST {&lt;AxisID&gt; &lt;StageName&gt;} set assignment of stages to axes
>
> &lt;&lt;CST? \[{&lt;AxisID&gt;}\] get assignment of stages to axes
>
> &lt;&lt;CSV? get current syntax version
>
> &lt;&lt;DEC? \[{&lt;AxisID&gt;}\]
>
> &lt;&lt;DFH \[{&lt;AxisID&gt;}\]
>
> &lt;&lt;DFH? \[{&lt;AxisID&gt;}\]
>
> &lt;&lt;ERR? get error number
>
> &lt;&lt;FED &lt;AxisID&gt; &lt;EdgeID&gt; &lt;param&gt;
>
> &lt;&lt;FNL \[{&lt;AxisID&gt;}\]
>
> &lt;&lt;FPL \[{&lt;AxisID&gt;}\]
>
> &lt;&lt;FRF \[{&lt;AxisID&gt;}\] fast reference move to reference switch
>
> &lt;&lt;FRF? \[{&lt;AxisID&gt;}\] get referencing result
>
> &lt;&lt;GOH {&lt;AxisID&gt;}
>
> &lt;&lt;HLP? get list of available commands
>
> &lt;&lt;HLT \[{&lt;AxisID&gt;}\] halt motion smoothly
>
> &lt;&lt;HPA? get list of available parameters
>
> &lt;&lt;IDN? get device identification
>
> &lt;&lt;INI \[{&lt;AxisID&gt;}\] initialize
>
> &lt;&lt;LIM? \[{&lt;AxisID&gt;}\] indicate limit switches
>
> &lt;&lt;MOV {&lt;AxisID&gt; &lt;Position&gt;} set target position (start absolute motion)
>
> &lt;&lt;MOV? \[{&lt;AxisID&gt;}\] get target position
>
> &lt;&lt;MVR {&lt;AxisID&gt; &lt;Distance&gt;} set target relative to current position (start relative motion)
>
> &lt;&lt;ONT? \[{&lt;AxisID&gt;}\] get on-target state
>
> &lt;&lt;POS {&lt;AxisID&gt; &lt;Position&gt;}
>
> &lt;&lt;POS? \[{&lt;AxisID&gt;}\] get real position
>
> &lt;&lt;RBT reboot system
>
> &lt;&lt;RON {&lt;AxisID&gt; &lt;ReferenceOn&gt;}
>
> &lt;&lt;RON? \[{&lt;AxisID&gt;}\] get reference mode
>
> &lt;&lt;SAI {&lt;AxisID\_Old&gt; &lt;AxisID\_New&gt;}
>
> &lt;&lt;SAI? \["ALL"\] get list of current axis identifiers
>
> &lt;&lt;SPA {&lt;ItemID&gt; &lt;PamID&gt; &lt;PamValue&gt;} set volatile memory parameters
>
> &lt;&lt;SPA? \[{&lt;ItemID&gt; &lt;PamID&gt;}\] get volatile memory parameters
>
> &lt;&lt;SRG? &lt;AxisID&gt; &lt;RegisterID&gt;
>
> &lt;&lt;STP stop all axes abruptly
>
> &lt;&lt;SVO {&lt;AxisID&gt; &lt;ServoState&gt;} set servo mode
>
> &lt;&lt;SVO? \[{&lt;AxisID&gt;}\] get servo mode
>
> &lt;&lt;TMN? \[{&lt;AxisID&gt;}\] get minimum commandable position
>
> &lt;&lt;TMX? \[{&lt;AxisID&gt;}\] get maximum commandable position
>
> &lt;&lt;TRS? \[{&lt;AxisID&gt;}\] indicate reference point switch
>
> &lt;&lt;TVI? tell valid character set for axis identifiers
>
> &lt;&lt;VEL {&lt;AxisID&gt; &lt;Velocity&gt;} set closed-loop velocity
>
> &lt;&lt;VEL? \[{&lt;AxisID&gt;}\] get closed-loop velocity
>
> &lt;&lt;VER? get version
>
> &lt;&lt;VST? list available stages
>
> &lt;&lt;WPA &lt;Password&gt; Save Parameters To Non-Volatile Memory

-   Sent command "MVR 1 3" via Command Entry in PIMikroMove -- microscope moved up

<!-- -->

-   PuTTY

    -   Serial connection on COM7, speed 19200, "z-stage" -- does not work

        -   "After you start up PuTTY in serial mode, you might find that you have to make the first move, by sending some data out of the serial line in order to notify the device at the other end that someone is there for it to talk to." -- from the manual

    -   Serial connection does not work on Windows 10 PC either

    -   PLINK immediately closes itself after launch

-   Virtual COMs?

-   Toshiba w/ RS232

    -   Install linux

>  
>
>

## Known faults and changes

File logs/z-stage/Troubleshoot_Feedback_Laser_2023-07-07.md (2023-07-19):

Troubleshoot\_Feedback\_Laser\_2023-07-07

Friday, July 7, 2023

7:47 PM

Feedback laser

-   Removed screws on panel front of Beam Deflector Laser module to check for poor electrical connection. The switch, laser input, and power LED connections to panel were attached from the inside, preventing the panel from being removed without severing the wires.

-   Potentially able to be accessed from the panel back? Two screws located underneath the padding on the back blue frame might open back panel. High voltage components so I will need to be grounded and extremely careful of capacitors.

405nm diode laser as substitute?

-   Datasheet says 30mW power output. Used THORLABS PM50 analog power meter to measure power at fiber output: ~25mW. Fiber is attached to the interior components of the laser and is therefore not able to be removed.

-   alphaSNOM manual says feedback laser is (785 ± 15) nm and between 1 and 5 mW. Will probably have to use ND filter on the 405 as the manual doesn't have any specs on the photodetector. Also, photodetector material may not respond to wavelengths under 700.

Update: Beam deflection laser \*does\* work. Measuring its power output via the analog power meter gives power reading of about 4 mW but does not appear to be on as it is likely a substituted laser in the near-IR (980 nm). One of the AlphaSNOM manuals lists this as a possible laser wavelength (the other lists 785nm).

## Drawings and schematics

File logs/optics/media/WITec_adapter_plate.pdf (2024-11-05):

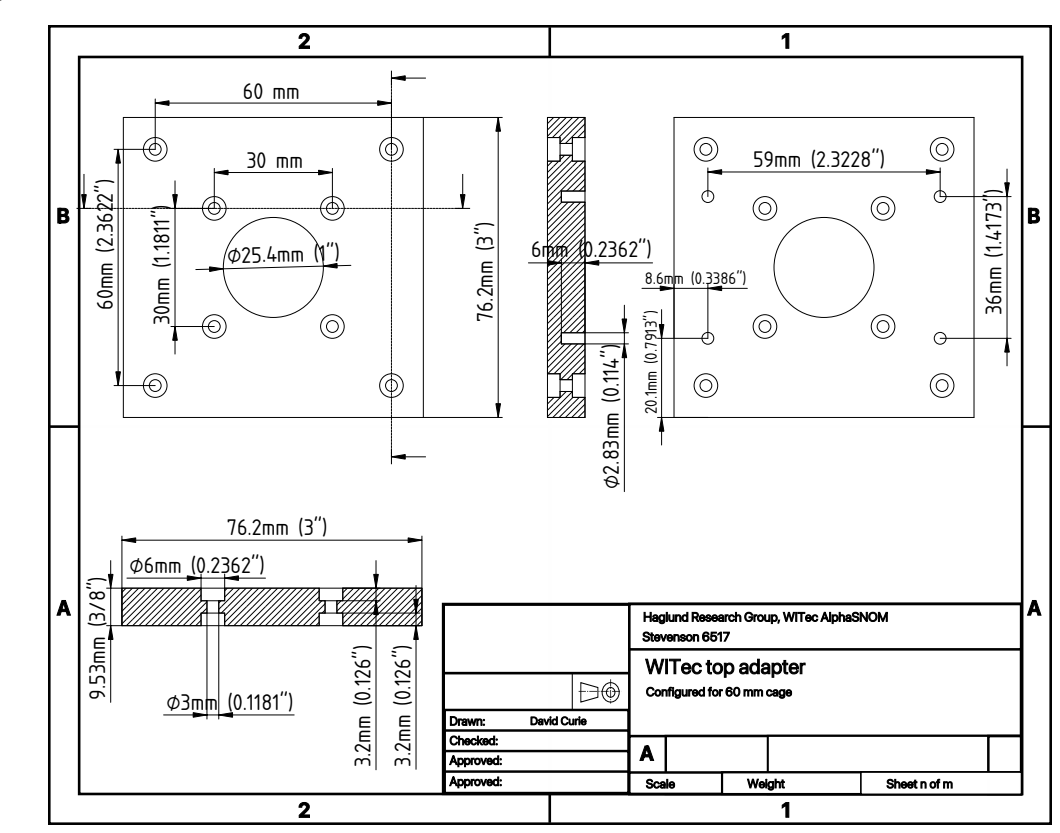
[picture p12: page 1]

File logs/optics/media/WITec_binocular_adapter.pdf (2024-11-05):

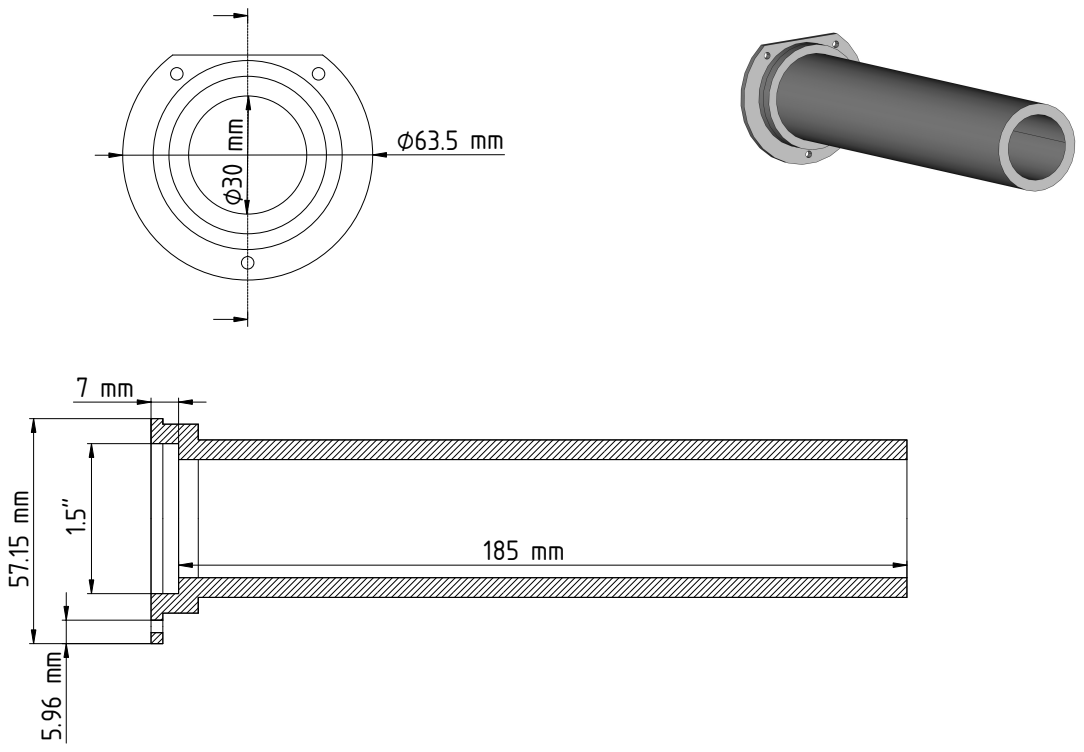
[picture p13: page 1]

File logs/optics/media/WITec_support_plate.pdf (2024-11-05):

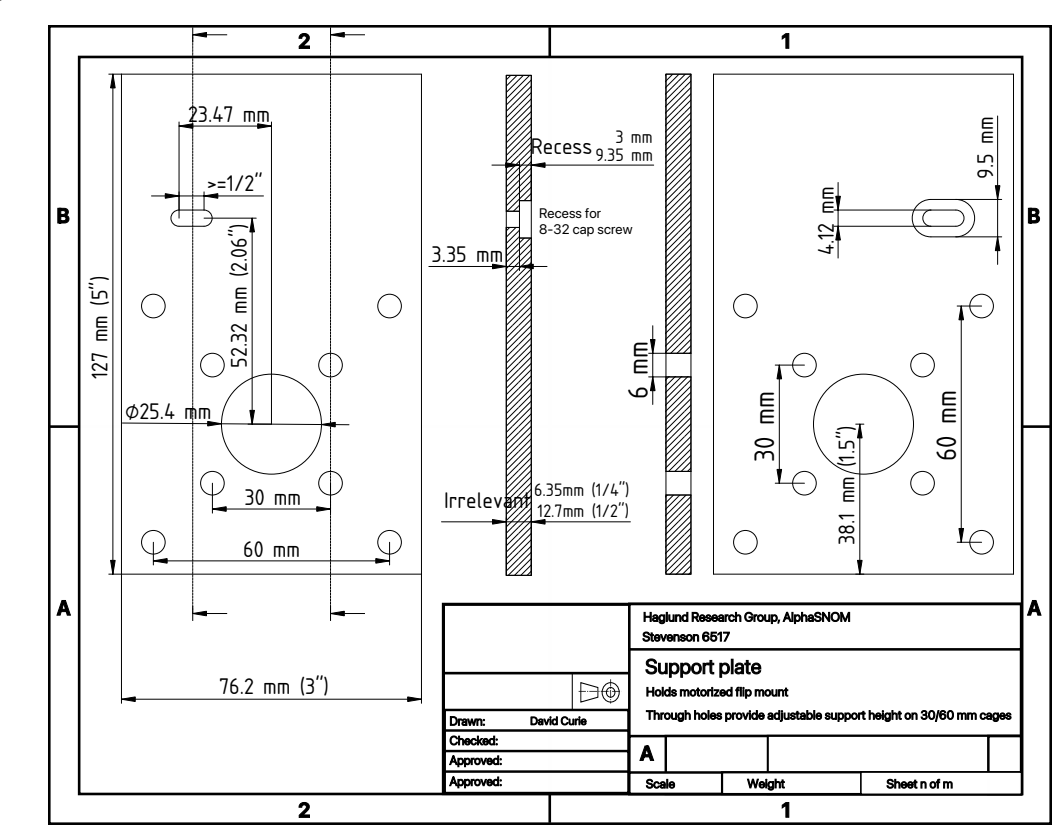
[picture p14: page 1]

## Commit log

2023-06-10 Add initial logs for optics assembly
    Submit a backlog of previously recorded data for version control. This
    data corresponds to power reading measurements at various points along
    the optical path for various excitation sources, including the Verdi V5
    laser.
2023-06-15 Document Princeton Instruments manuals
    Link PDF versions of spectrometers, accomapying cameras, and legacy
    software in use by the WITec AlphaSNOM.
2023-06-15 Document Coherent manuals for Verdi laser
    Link PDF versions of the manuals in the how-to guide.
2023-06-23 Document PI micos commands and user manuals
    Add Venus commands for low-level communication over serial port, a
    software user manual to control the focus of the WITec AlphaSNOM,
    and a technical manual of the elevation stage.
2023-06-23 Start z-stage third-party improvements
    Document a plan to use the third-party PI-micos stage with AFM and NSOM
    functionality.
    AFM and NSOM are available in ScanCtrlSpectroscopyPlus but depend on the
    OEM stage being connected properly. The OEM stage died and no identical
    replacement exists. The hardware to support AFM and NSOM still exists on
    the WITec AlphaSNOM, but we'll need customized scripts to allow the
    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
2023-06-23 Document z-stage daily log
2023-09-13 Fix document Verdi SOP to update shut down temp
    The offical instructions say to wait until the LBO crystal reads 40
    degrees C before turning the back panel switch to OFF. This assumes a
    working battery to maintain the remaining cooldown procedure on battery
    power. The battery as of September 2023 does not hold a charge, so make
    the recommended minimum temperature lower before resuming a complete
    shut down.
2023-09-22 Fix document Verdi SOP to use Vanderbilt template
    The previous SOP is more of a quick start guide for daily operation.
    Its contents have been moved to verdi_quick-start.md. The new SOP
    follows the guidelines set forth by the Vanderbilt laser safety office
    and is modeled after their provided Word template.
2023-09-22 Optimize datetime assignment to handle timezones
    Rewrite the datetime assignment to use a simpler algorithm that doesn't
    involve assigning datetime fields by sequence position in a string.
    While the previous solution handles any combination of YYYY-MM-DD
    format with generally unspecified separators, it cannot easily pick out
    the case where a datetime sometimes has timezone information and
    sometimes does not. It also does not allow for permutations of the
    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
2023-09-22 Reword Witec class variables
    magic -> file_type
    dict -> contents
    The extracted dictionary of data from the .WIP file is now accessed from
    a wip object as wip.contents instead of wip.dict. Future refactoring
    efforts aim to supply meaningful shortcuts to the nested hierarchy of
    data with short attributes like wip.data and wip.info, the results of
    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
2023-09-22 Document Verdi enclosure
    Provide measurements for reproducible light-tight enclosure box for the
    Verdi-V5 laser.
2024-01-18 Fix Document Coherent manuals for Verdi laser
    Replace V8/V10 manual with V2/V5/V6 manual.
    Reference V5 manual found at:
    http://ull.tju.edu.cn/education/manual/verdi.manual_v5.pdf
2024-01-26 Document investigation of laser output quality
    Begin documenting efforts to clean up Verdi-V5 laser output.
2024-01-27 Document laser LBO optimization
    Log settings before and after LBO crystal optimization in an attempt to
    refine laser output.
2024-02-01 Document laser alignment
    Adjust single-mode fiber coupling at Verdi-V5 output and update remarks
    on laser throughput.
2024-02-04 Document free-space laser investigation
    Log efforts made to better understand the Verdi laser output.
2024-02-17 Document laser line filter testing
    Log progress on efforts to clean up laser line.
2024-02-22 Document laser line filter placement
    Describe the permanent location of the laser line filter inserted into
    the back of the WITec microscope and provide instructions on how to
    access this filter in the future.
    [assembly_filter-holder.step]
2024-11-09 Document laser power hysteresis
    Log the effect of diode current on measured power output.
2024-11-12 Document laser alignment
    Investigate the effects at the sample of misalignment at the single-mode
    fiber entrance. Return to optimal alignment and report the benchmark
    power readings throughout the beam path.
2024-11-13 Document laser stability
    Log the laser power from startup to track the time it takes to stabilize
    and to determine the long-term stability over several hours.
2024-11-19 Document spectrometer calibration
    Log the calibration date of Acton 300i spectrometer.
2024-12-06 Document laser power at the sample
    Log laser power at under the microscope objectives at various set powers
    and ND filter arrangements
2024-12-07 Document laser power at the sample
    Log the laser power under the objectives for
    various laser powers and ND filters situated in a new orientation.
    Duplicate these measurements during ramp up and ramp down in established
    laser power.
2025-01-21 Fix 42bd013 Add initial logs for optics assembly
    The figure for laser power readings did not generate from build tools
    because of a typo in the plotting routine. Now the figure can be built
    without failure.
2025-01-25 Add SMCPollux class to interact via Venus2
    Use the Venus2 ASCII protocol to manually send commands to the SMC
    Pollux box.
    micos.py introduces a class to act as a Python wrapper around the known
    Venus2 commands. stage.py shows how one might use micos in action.
